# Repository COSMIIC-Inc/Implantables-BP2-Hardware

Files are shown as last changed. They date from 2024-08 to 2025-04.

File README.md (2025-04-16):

# Implantables-BP2-Hardware Read Me

## Contents
This repository is home to the 3D CAD and PCB design files of the BP2 - Biopotential Recording Module in the COSMIIC System.
Further documentation is available at **[docs.cosmiic.org/Implantables/BP2-Module](https://docs.cosmiic.org/Implantables/BP2-Module)**

## Licensing
Hardware-related files are licensed to open source users by COSMIIC under the CERN Open Hardware License - Permissive - v2 (CERN-OHL-P-2.0). Refer to the **[license text](https://ohwr.org/cern_ohl_p_v2.txt)** (also embedded in the repository as **LICENSE.txt**) and **[user guide](https://ohwr.org/project/cernohl/-/wikis/uploads/8a6b5d01f71c207c49493e4d114d61e6/cern_ohl_p_v2_howto.pdf)** to understand your permissions.

Hardware-related files includes, but is not limited to...

- Mechanical Design
    - 3D CAD Files (parts and assemblies, multiple file types)
    - Mechanical Drawings (parts and assemblies, mulitple file types)
- PCB Design
    - Fabrication (Gerber and Drill files)
    - Assembly (Pick and Place, BOM)
    - Archive (Schematics, multiple file types)

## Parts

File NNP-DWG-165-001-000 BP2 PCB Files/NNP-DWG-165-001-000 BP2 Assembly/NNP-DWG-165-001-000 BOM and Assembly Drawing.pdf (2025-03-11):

D | D

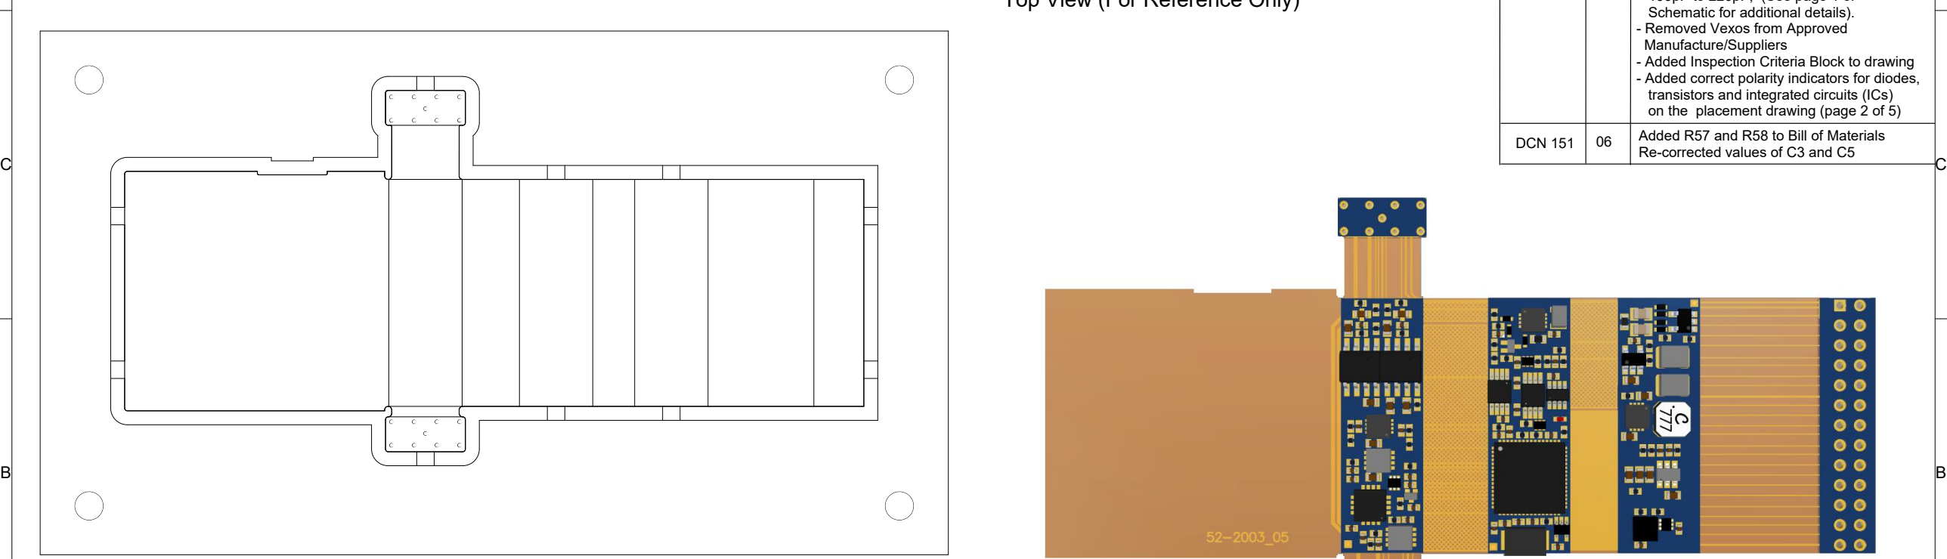
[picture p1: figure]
Schematic for additional details). - Removed Vexos from Approved Manufacture/Suppliers; transistors and integrated circuits (ICs) on the placement drawing (page 2 of 5); Re-corrected values of C3 and C5; DCN 151
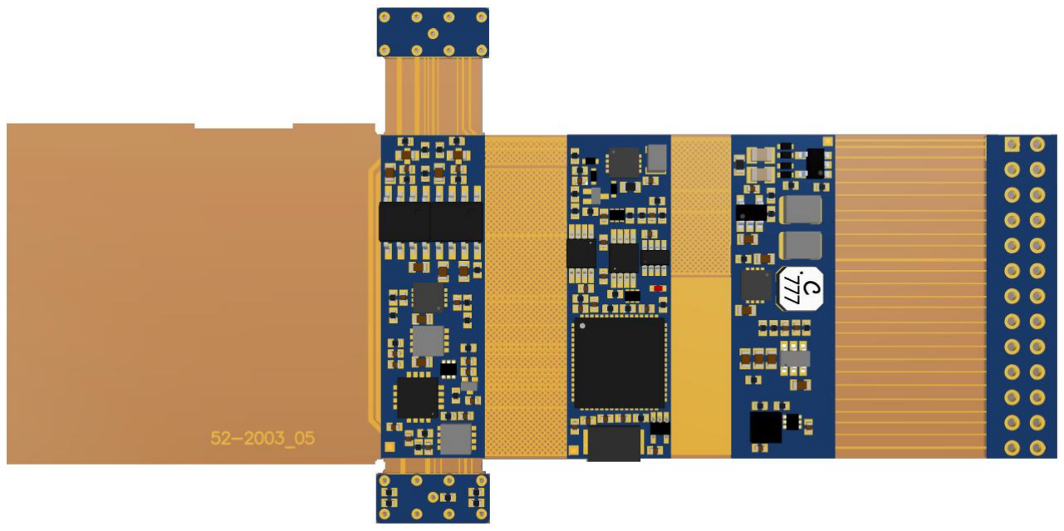
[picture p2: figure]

A | A
DRAWN K. Kowalski | 11-18-2022
CHECKED T. Crish | 11-18-2022
51-2003 | 06

Biopotential (BP2) PCB Assembly Drawing

DOCUMENT NAME

DOCUMENT NO. | REV

NEXT ASSY
SCALE:

B

SIZE
FINISH

MATERIAL

BY | DATE

SHEET 1 OF 5

ECN | REV | DESCRIPTION

N/A

1. Approved Manufacture/Suppliers.
Valtronic Technologies
2. Appropriate ESD precautions shall be used while building or handling this assembly.
3. PCB, Components and Solder must be RoHS 2 compliant.
4. Assembly shall be acceptable and rejectable per IPC-A-610, Class 3.
5. Components with pin 1 designator or polarization marking shall be placed as indicated on the assembly drawing.
6. Rework, repair or modifications must comply with IPC-7711 and IPC 7721.
7. Each PCB must be sequentially serialized and labeled as indicated on the purchase order.
8. Must supply testing certificate with every PCB assembly lot.
9. Supplier must notify and receive approval from Synapse Biomedical Inc before making any modifications to the design process or any changes to the materials used during the manufacturing of this assembly.
10. Do not populate C18, R26, and U10.
11. Do not populate R1-R10
12. Printed circuit boards (PCBs) shall be shipped in frames.
13. R57 is hand-soldered across pins 4 and 5 of U12.
14. R58 is hand-soldered across the gate and source of Q2.

Equivalent to CWRU VT901002

Build for BP2C Verification
- Removed Power-up reset circuit.
- Changed values of C1, C3, C5 and C6

DCN 101 03

- Updated BOM (refer to Page 1 of the Schematic for changes)
- Updated Manufacturing Notes
- Added PCB Frame and Outline Drawings
- Added instructions for serial number sticker.
- Added quantity to the BOM.
- Removed Software reference.
- Removed Inspection Criteria Block

DCN 107 04

N/A

DCN 121 05

- Add Pick and Place file to the BOM.
- Changed Capacitors C40 and C51 from 100pF to 220pF, (See page 1 of
- Added Inspection Criteria Block to drawing
- Added correct polarity indicators for diodes,

N/A

## Top View (For Reference Only)

E

INSPECTION REQUIRED | YES | NO
| X
CERTIFICATE REQUIRED | YES | NO
| X

Insp. Item
A | Inspect to current 51-2003-08 Inspection Procedure
| REF 51-2003-09 Inspect report
C | RoHS Certificate required

D

INSPECTION CRITERIA

06 Added R57 and R58 to Bill of Materials

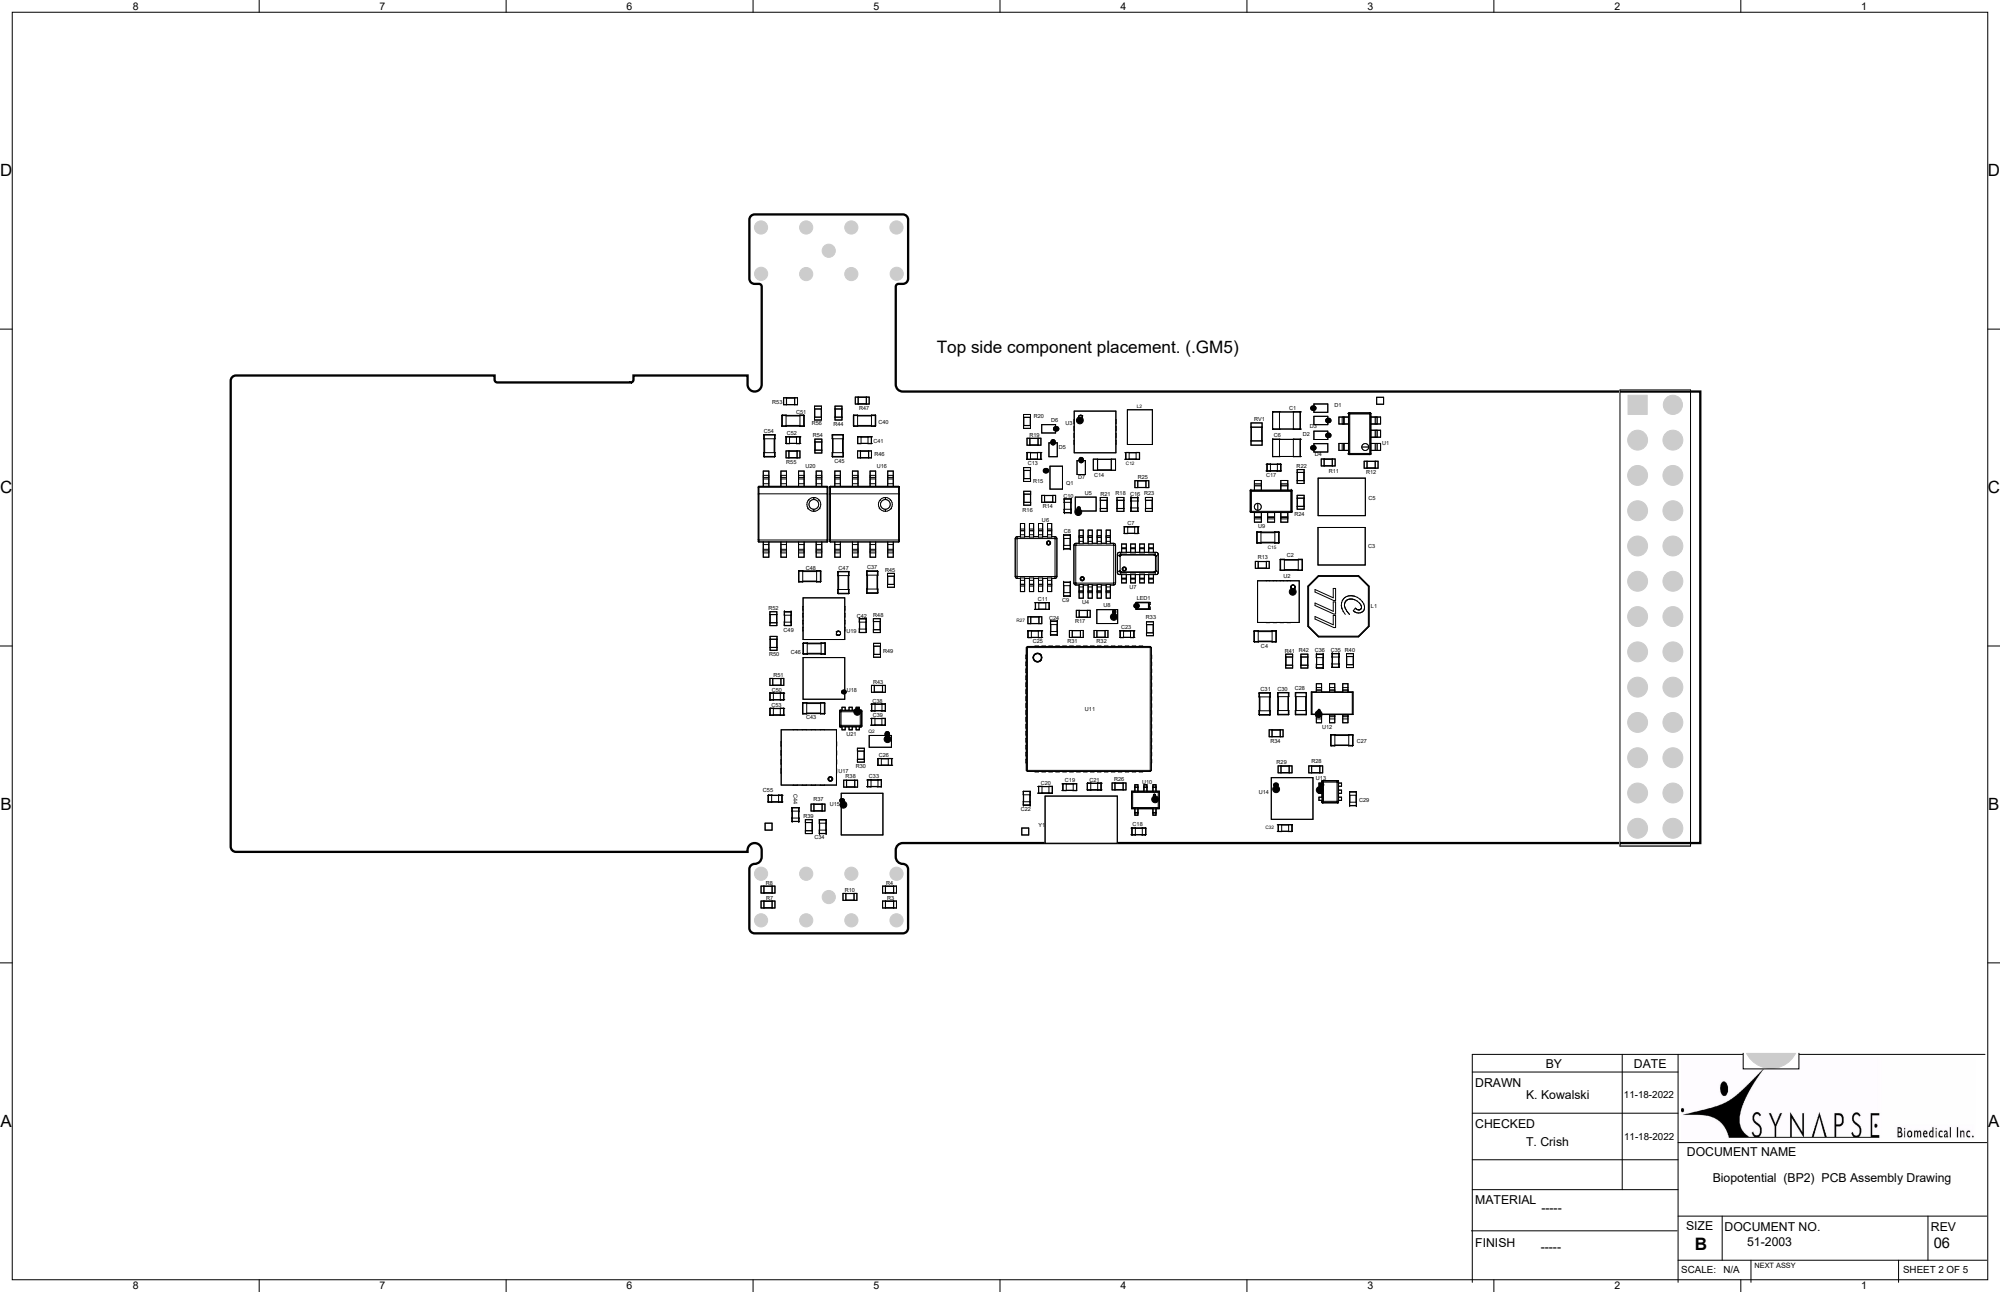
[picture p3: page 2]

Top side component placement. (.GM5)

DRAWN K. Kowalski | 11-18-2022

CHECKED T. Crish | 11-18-2022

DOCUMENT NAME
Biopotential (BP2) PCB Assembly Drawing

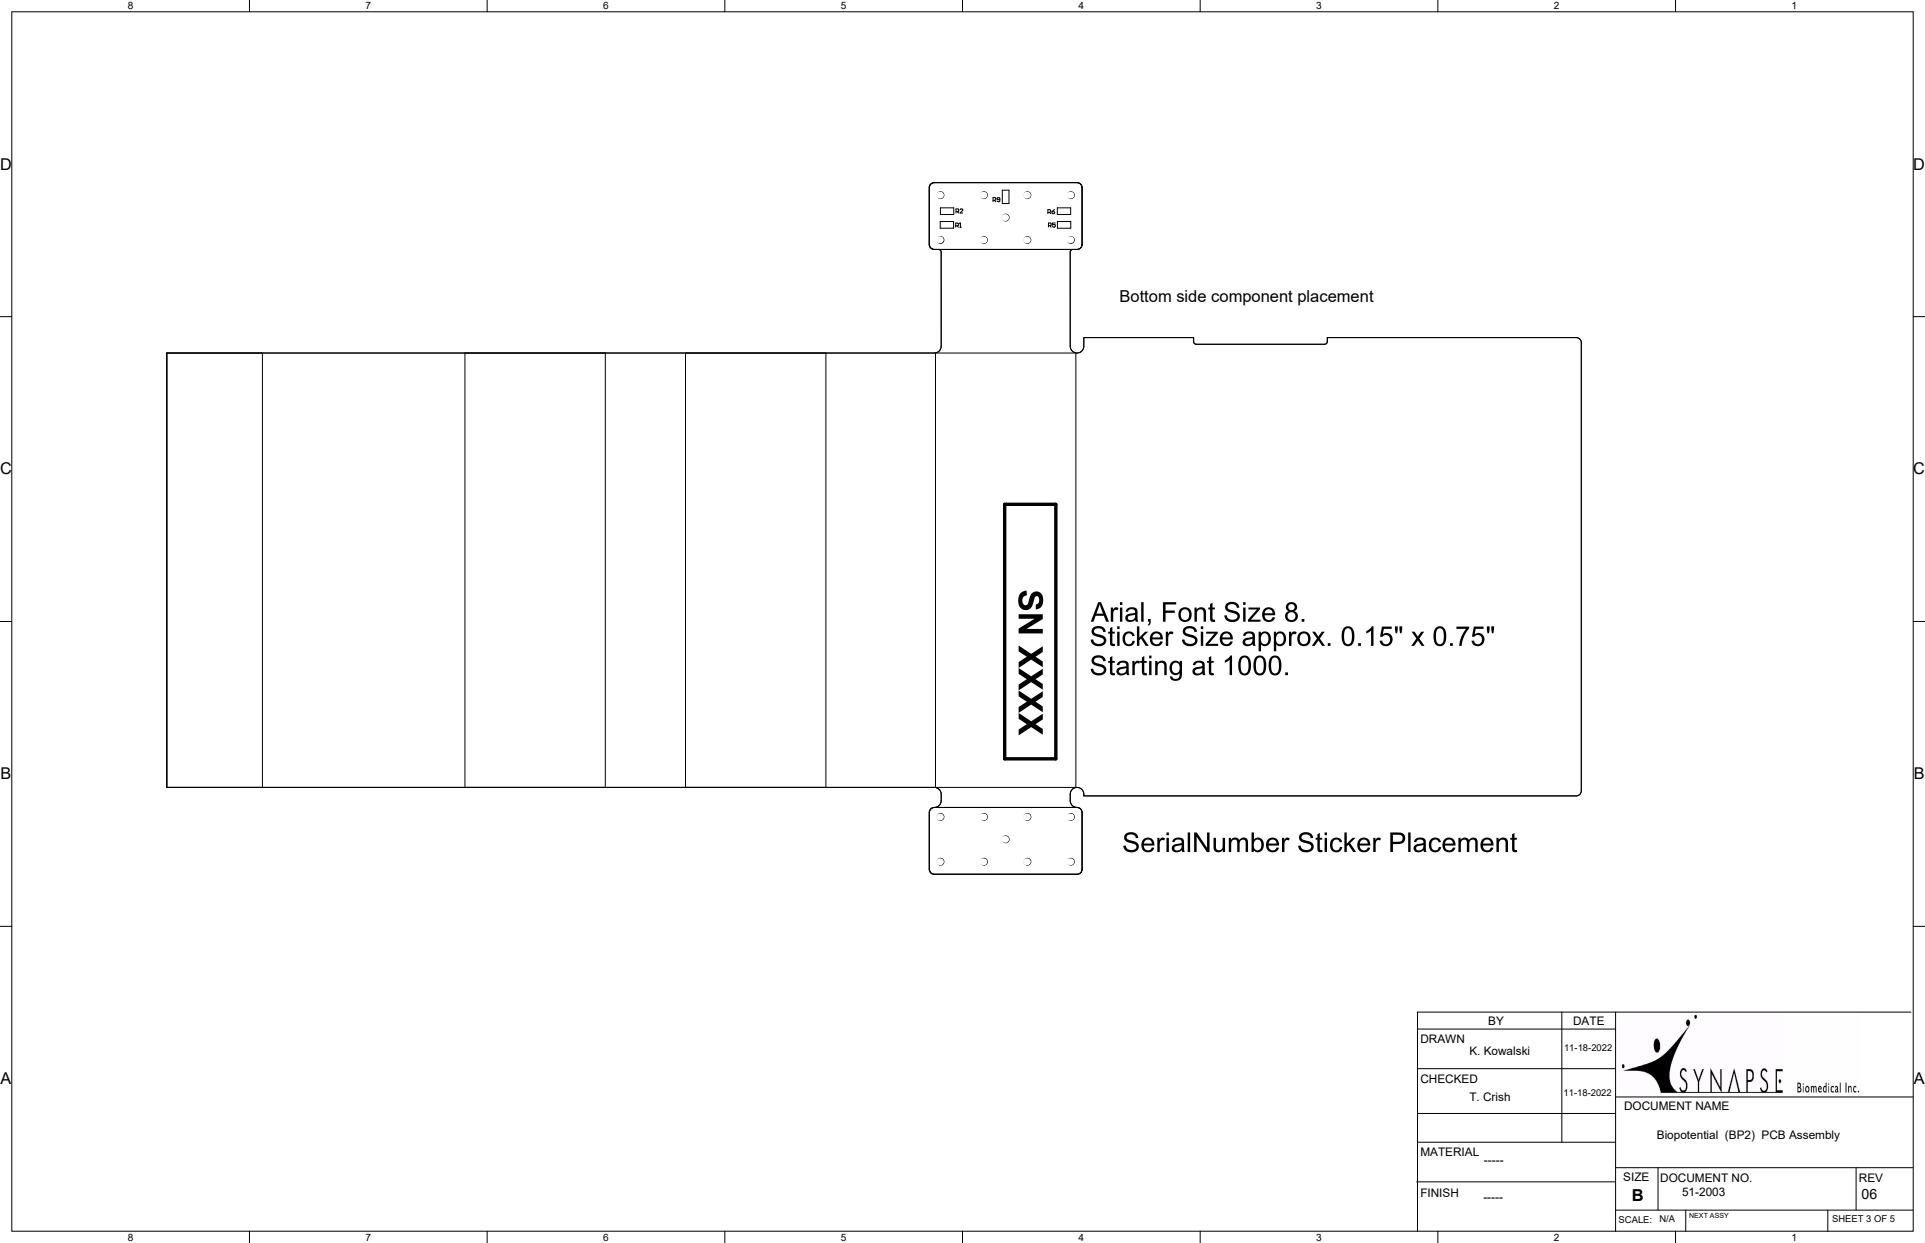
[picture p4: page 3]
DATE; DOCUMENT NAME

Bottom side component placement

DRAWN K. Kowalski | 11-18-2022

CHECKED T. Crish | 11-18-2022

Biopotential (BP2) PCB Assembly

D | D
C | C
B | B
A | A
BY | DATE
DRAWN K. Kowalski | 11-18-2022
CHECKED T. Crish | 11-18-2022

DOCUMENT NAME

Biopotential (BP2) PCB Assembly

Item

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
Designator

Ref.

Ref.

Ref.

C1, C6
C2, C14, C15, C28, C30, C31
C3, C5
C4, C27
C7, C8, C9, C10, C11, C20, C22, C23, C24, C29, C32, C34, C35, C38, C39, C42, C49, C50, C53
C12, C16
C13
C17
C19, C21
C25
C37, C43, C45, C46, C47, C48, C54 C36
C40, C51
C41, C52
C33, C44, C55
C26
D1, D2, D3, D4, D5, D6, D7 L1
L2
LED1
Q1

Q2

R1, R2, R3, R4, R5, R6, R7, R8, R9, R10 R11
R12, R17, R18, R19, R22, R25, R42 R13
R14, R20, R21, R23

SBI

51-2003-01_07

52-2003_05

51-2003-07_02

53-0097
53-0067
53-0068
53-0039
53-0040-1

53-0042
53-0041-1
53-0043
53-0044-1
53-0069
53-0070
53-0041-2
53-0071
53-0072
53-0040-2
53-0078
54-0075
53-0032
53-0033
53-0035
54-0050

54-0078

53-0048
53-0049-1
53-0049-2
53-0049-3
53-0049-4

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
Description

Biopotential (BP2) Schematic Drawing 51-2003-01_07
NNP Biopotential PCB, Unpopulated 52-2003_05
Biopotential (BP2) Pick and Place 51-2003-07_02 Biopotential (BP2) 0.1uF, 100V, X7R, 0805, 10%, RoHS 1.0uF, 50V, X7R, 0603, 20%, RoHs 22uF, 16V, X5R, 1210, 20%, RoHS 10uF, 6.3V, X5R, 0603_20%, RoHS 0.1uF, 16V, X7R,10%, 0402, RoHS

4.7uF, 6.3V, X5R, 20%, 0402, RoHS 68pF, 50V, C0G, 0402, 5%, RoHS 0.001uF, 50V, X7R, 20%, 0402, RoHS 8pF, 50V, C0G, 0402, 10%, RoHS 2.2uF, 6.3V, X5R, 0402, 20%, RoHS 0.15uF, 16V, X7R, 10%, 0603, RoHS 1000pF, 50V, C0G, 5%, 0402, RoHS X2Y, 220pF, 50V, X7R, 0603, 20%, RoHS 4700pF, 50V, C0G, 0402_10%, RoHS 0.15uF, 16V, X7R, 10%, 0402, RoHS 1.0uF, 6.3V, X5R, 0402, 20%, RoHS Schotty Diode, 30V, 100mA, RoHS 100uH, 270mA, 20%, RoHS
470uH, 35mA, 10%, RoHS
LED, Red, 0402, 20mA ,2V, 140mcd, RoHS PNP, -50V, -100mA, SOT523, 150MHz, RoHS
Small Signal MOSFET, -20 V, -760 mA, P-Channel, Gate Zener
0.0 ohm, 1/16W, 0402, RoHS
0.1 ohm, 1%, 1/16W, 0402, RoHS
49.9k ohm, 1%, 1/16W, 0402, RoHS 470k ohm, 1% , 1/16W, smd, 0402, RoHS 1.0k ohm, 1%, 1/16W, smd, 0402, RoHS

Manufacture

N/A

See Note 1

N/A

Murata Electronics North America Taioyo Yuden
Taioyo Yuden
Murata Electronics North America Murata Electronics North America

Murata Electronics North America Murata Electronics North America Murata Electronics North America Murata Electronics North America Murata Electronics North America Samsung-Electro-Mechanics
Murata Electronics North America Johanson Dielectrics Inc.
Murata Electronics North America Samsung-Electro-Mechanics
Murata Electronics North America Panasonic Electronic Components TDK Corporation
Taiyo Yuden
Lumex Opto/Components Inc. Panasonic Electronic Components

ON Semiconductor

Vishay Dale
Vishay Dale
Vishay Dale
Vishay Dale
Vishay Dale

Manufacturer Part Number

N/A

N/A

N/A

GCM21BR72A104KA37K
UMK107AB7105KA-T
EMK325BJ226MD-T
GRM188R60J106ME47J
GRM155R71C104KA88D

GRM155R60J475ME47D
GRM1555C1H680JA01D
GJM1555C1H1R0BB01D
GRM1555C1H8R0DA01D
GRM155R60J225ME15D
CL05B154KO5NNNC
GRM1555C1H102JA01D
500X14W221MV4T
GRM155R71H472KA01D
CL05B154KO5NNNC
GRM155R60J105ME19D
DB2731600L
VLCF5020T-101MR27
CB2518T471K
SML-LX0402SIC-TR
DSA9001S0L

NTE4151PT1G

CRCW04020000Z0ED
RCWE0402R100FNEA
CRCW040249K9FKED
CRCW0402470KFKED
CRCW04021K00FKED

Suggested
Supplier
N/A

See Note 1

N/A

Digi-Key
Digi-Key
Digi-Key
Digi-Key
Digi-Key

Digi-Key
Digi-Key
Digi-Key
Digi-Key
Digi-Key
Digi-Key
Digi-Key
Digi-Key
Digi-Key
Digi-Key
Digi-Key
Digi-Key
Digi-Key
Digi-Key
Digi-Key
Digi-Key

Digi-Key

Digi-Key
Digi-Key
Digi-Key
Digi-Key
Digi-Key

Supplier Part Number

N/A

N/A

N/A

490-8051-2-ND
587-5956-6-ND
587-2412-1-ND
490-6405-6-ND
490-3261-6-ND

490-5915-6-ND
490-5876-6-ND
490-6073-6-ND
490-5867-6-ND
490-4519-6-ND
1276-6651
490-3244-6-ND
500X14W221MV4T-ND
490-1308-6-ND
1276-6651-6-ND
490-5955-6-ND
DB2731600LDKR-ND
445-3203-6-ND
587-2194-6-ND
67-1878-6-ND
DSA9001S0LDKR-ND

NTE4151PT1GOSDKR-ND

541-0.0JDKR-ND
541-2711-6-ND
541-49.9KLDKR-ND
541-470KLDKR-ND
541-1.00KLDKR-ND

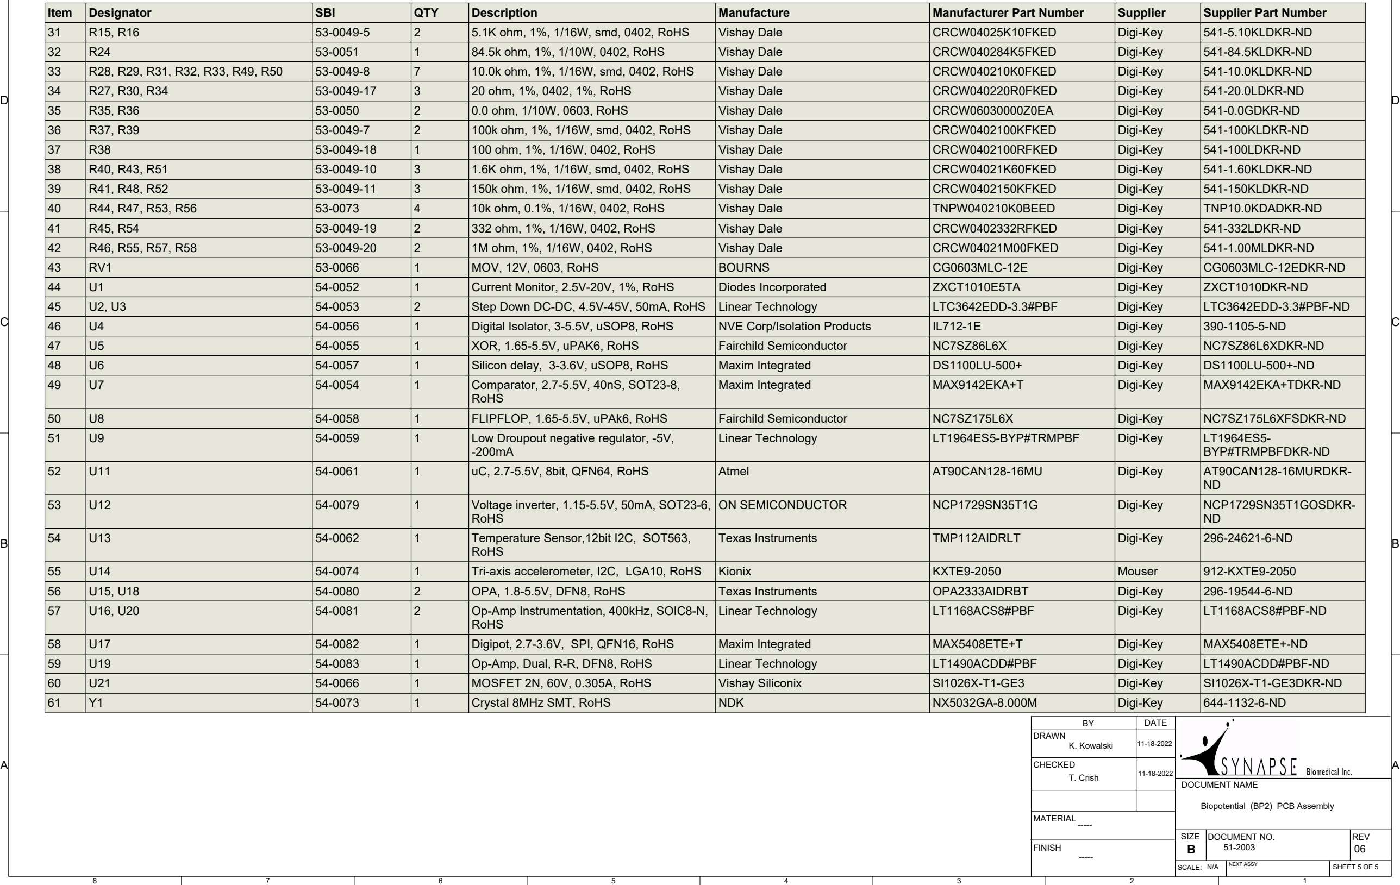
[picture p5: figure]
DATE; CHECKED T. Crish; DRAWN K. Kowalski; DOCUMENT NAME; Biopotential (BP2) PCB Assembly; Item; Designator R15, R16 R24 R28, R29, R31, R32, R33, R49, R50 R27, R30, R34 R35, R36 R37, R39 R38 R40, R43, R51 R41, R48, R52 R44, R47, R53, R56 R45, R54 R46, R55, R57, R58 RV1 U1 U2, U3 U4 U5 U6 U7; SBI 53-0049-5 53-0051 53-0049-8 53-0049-17 53-0050 53-0049-7 53-0049-18 53-0049-10 53-0049-11 53-0073 53-0049-19 53-0049-20 53-0066 54-0052 54-0053 54-0056 54-0055 54-0057 54-0054; QTY; Description 5.1K ohm, 1%, 1/16W, smd, 0402, RoHS 84.5k ohm, 1%, 1/10W, 0402, RoHS 10.0k ohm, 1%, 1/16W, smd, 0402, RoHS 20 ohm, 1%, 0402, 1%, RoHS 0.0 ohm, 1/10W, 0603, RoHS 100k ohm, 1%, 1/16W, smd, 0402, RoHS 100 ohm, 1%, 1/16W, 0402, RoHS 1.6K ohm, 1%, 1/16W, smd, 0402, RoHS 150k ohm, 1%, 1/16W, smd, 0402, RoHS 10k ohm, 0.1%, 1/16W, 0402, RoHS 332 ohm, 1%, 1/16W, 0402, RoHS 1M ohm, 1%, 1/16W, 0402, RoHS MOV, 12V, 0603, RoHS Current Monitor, 2.5V-20V, 1%, RoHS Step Down DC-DC, 4.5V-45V, 50mA, RoHS Digital Isolator, 3-5.5V, uSOP8, RoHS XOR, 1.65-5.5V, uPAK6, RoHS Silicon delay, 3-3.6V, uSOP8, RoHS Comparator, 2.7-5.5V, 40nS, SOT23-8, RoHS FLIPFLOP, 1.65-5.5V, uPAk6, RoHS Low Droupout negative regulator, -5V, -200mA uC, 2.7-5.5V, 8bit, QFN64, RoHS; Voltage inverter, 1.15-5.5V, 50mA, SOT23-6, RoHS Temperature Sensor,12bit I2C, SOT563, RoHS Tri-axis accelerometer, I2C, LGA10, RoHS OPA, 1.8-5.5V, DFN8, RoHS Op-Amp Instrumentation, 400kHz, SOIC8-N, RoHS Digipot, 2.7-3.6V, SPI, QFN16, RoHS Op-Amp, Dual, R-R, DFN8, RoHS MOSFET 2N, 60V, 0.305A, RoHS Crystal 8MHz SMT, RoHS; Manufacture Vishay Dale Vishay Dale Vishay Dale Vishay Dale Vishay Dale Vishay Dale Vishay Dale Vishay Dale Vishay Dale Vishay Dale Vishay Dale Vishay Dale BOURNS Diodes Incorporated Linear Technology NVE Corp/Isolation Products Fairchild Semiconductor Maxim Integrated Maxim Integrated; Fairchild Semiconductor Linear Technology; Atmel; ON SEMICONDUCTOR; Texas Instruments; Kionix Texas Instruments Linear Technology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

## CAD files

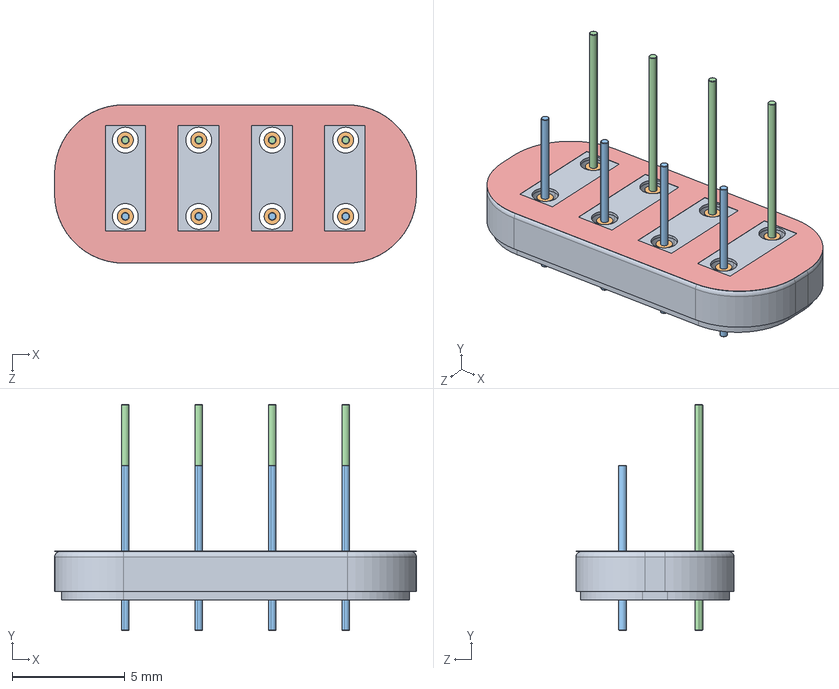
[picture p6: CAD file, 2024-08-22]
Mechanical Design CAD Files/STEP Files/NNP-DWG-135-001-001 SA, Remote Module, Capthrough Sandblasted.STEP
16.0 x 10.0 x 7.01 mm
NNP-DWG-130-010-000 Remote Module, Capthrough, Lid
NNP-DWG-130-008-000 Capthrough, Ceramic x 8
NNP-DWG-130-009-001 Capthrough, Pin, Ring x 4
NNP-DWG-130-009-002 Capthrough, Pin, Jogged_PRE-BENT x 4
NNP-MAT-150-017-000 150 Micron Aluminum Oxide

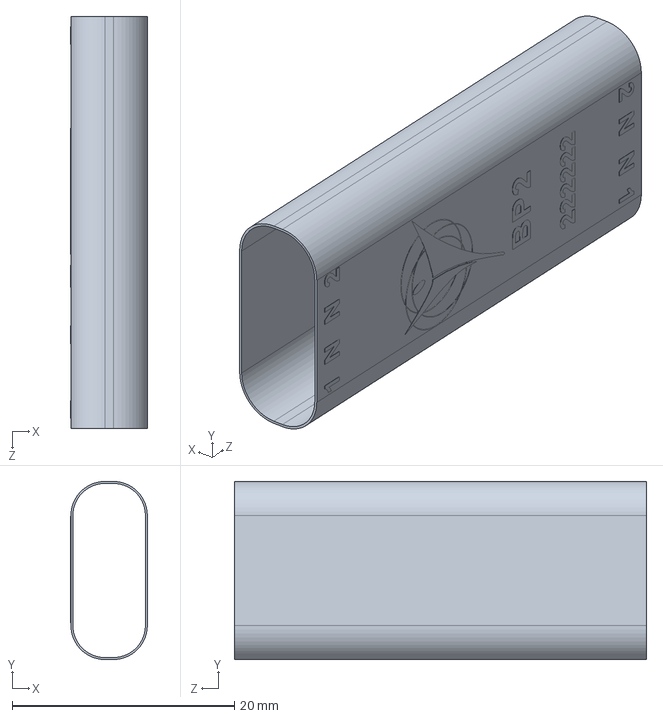
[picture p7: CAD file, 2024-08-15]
Mechanical Design CAD Files/STEP Files/NNP-DWG-160-001-000 Remote Module, Case, BP2 Marking.STEP
6.91 x 16.0 x 37.1 mm

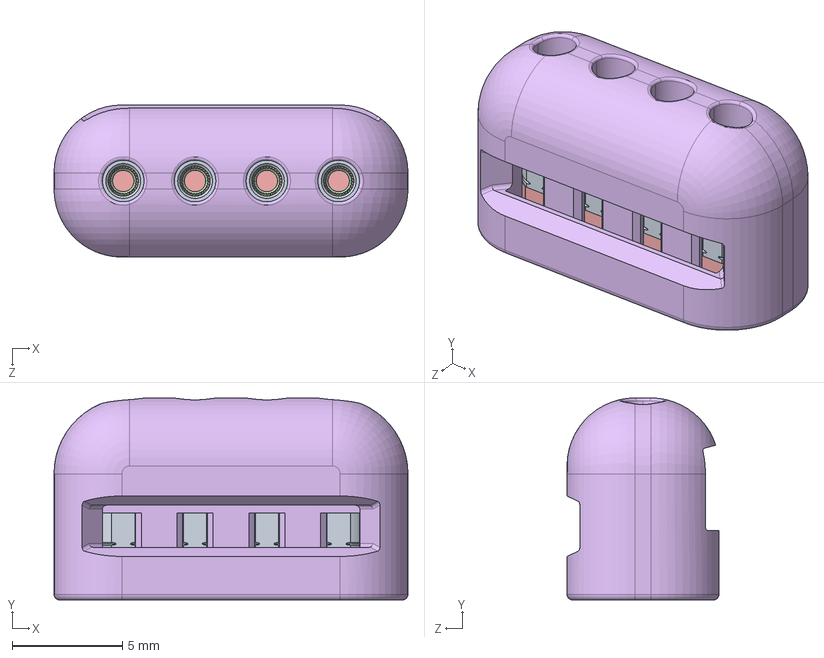
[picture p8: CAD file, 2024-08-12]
Mechanical Design CAD Files/STEP Files/NNP-DWG-135-005-000 SA, Remote Module, Header.STEP
16.0 x 9.14 x 6.88 mm
NNP-DWG-130-011-000 Balseal, Conductor x 8
NNP-DWG-130-012-001 Balseal, Spring, CW x 4
NNP-DWG-130-013-001 Balseal, Washer, CW x 4
NNP-DWG-130-013-002 Balseal, Washer, CCW x 4
NNP-DWG-130-012-002 Balseal, Spring, CCW x 4
NNP-DWG-130-005-000 BalSeal Assembly, Internal Cavity Single Seal_COMPRESSED x 4
NNP-DWG-130-004-000 Remote Module, Pre-Molded Header Cap
NNP-DWG-130-003-000 Remote Module, Pre-Molded Header Body
NNP-DWG-130-006-000 Remote Module, Header, Gasket_GASKET x 8

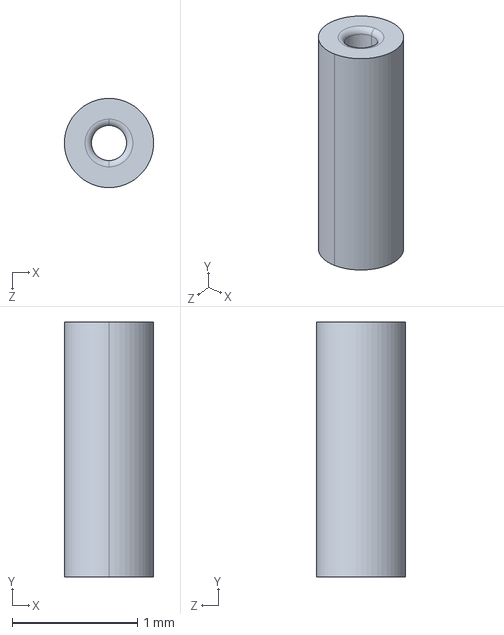
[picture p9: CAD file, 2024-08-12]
Mechanical Design CAD Files/STEP Files/NNP-DWG-130-008-000 Capthrough, Ceramic.STEP
0.711 x 2.03 x 0.711 mm

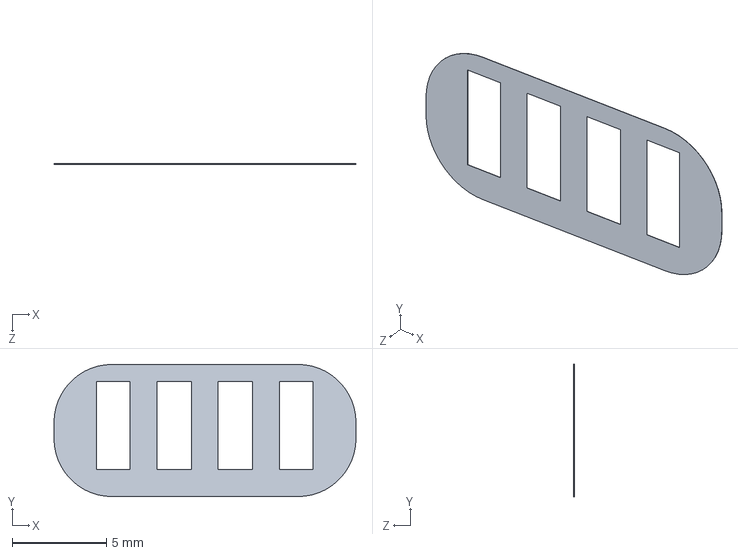
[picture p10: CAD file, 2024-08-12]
Mechanical Design CAD Files/STEP Files/NNP-MAT-150-017-000 150 Micron Aluminum Oxide.STEP
16.0 x 7.01 x 0.0127 mm

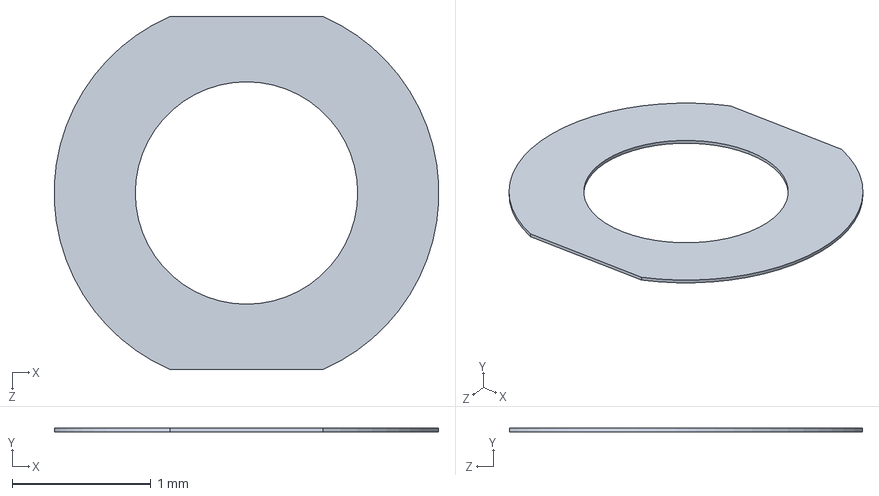
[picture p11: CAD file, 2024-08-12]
Mechanical Design CAD Files/STEP Files/NNP-DWG-130-006-000 Remote Module, Header, Gasket.STEP
2.77 x 0.0254 x 2.54 mm

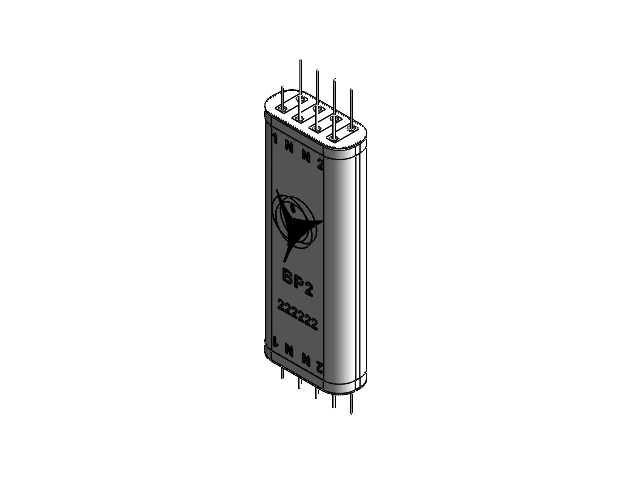
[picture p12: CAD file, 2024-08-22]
Mechanical Design CAD Files/SolidWorks Native Files/NNP-DWG-165-002-001 SA, BP2 Module, Tack Weld Assembly.SLDASM
NNP-DWG-130-001-000 Remote Module, Case
NNP-DWG-130-010-000 Remote Module, Capthrough, Lid x 2
NNP-DWG-130-008-000 Capthrough, Ceramic x 16
NNP-DWG-130-009-001 Capthrough, Pin, Ring x 8
NNP-DWG-130-009-002 Capthrough, Pin, Jogged x 8
NNP-MAT-150-017-000 150 Micron Aluminum Oxide x 2
NNP-MAT-150-008-000 EPO-TEK 301 x 2
NNP-DWG-165-001-000 Remote Module, BP2, Flexible Circuit Assembly
NNP-DWG-130-002-000 Remote Module, Insulator Flex x 2
NNP-MAT-150-006-000 70% Isopropyl Alochol x 2
NNP-MAT-150-005-000 Distilled Water

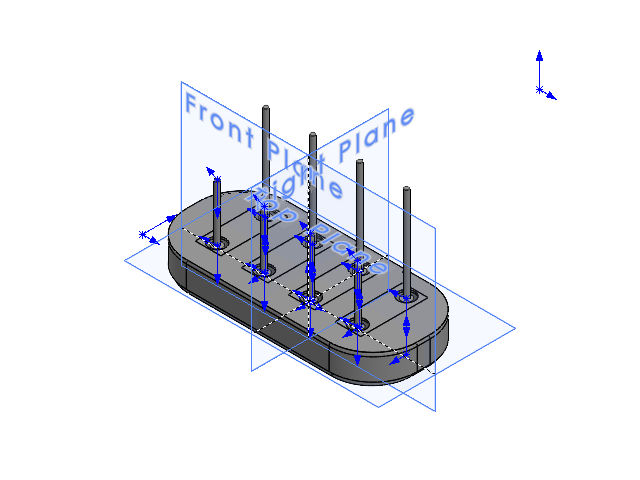
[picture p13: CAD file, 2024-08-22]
Mechanical Design CAD Files/SolidWorks Native Files/NNP-DWG-135-001-001 SA, Remote Module, Capthrough Sandblasted.SLDASM
NNP-DWG-130-010-000 Remote Module, Capthrough, Lid
NNP-DWG-130-008-000 Capthrough, Ceramic x 8
NNP-DWG-130-009-001 Capthrough, Pin, Ring x 4
NNP-DWG-130-009-002 Capthrough, Pin, Jogged x 4
NNP-MAT-150-017-000 150 Micron Aluminum Oxide
NNP-MAT-150-008-000 EPO-TEK 301

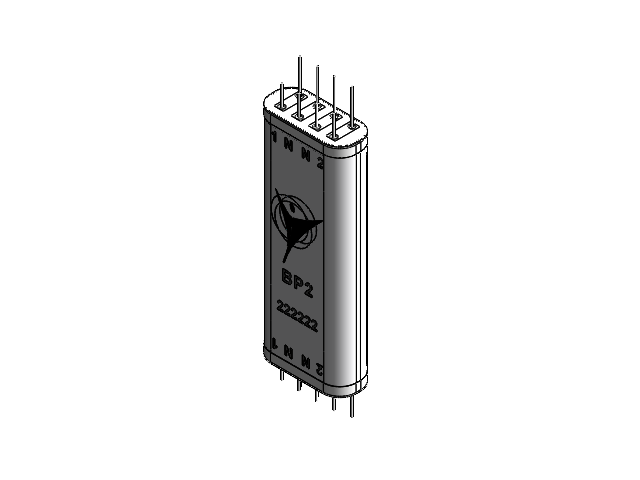
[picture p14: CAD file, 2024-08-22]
Mechanical Design CAD Files/SolidWorks Native Files/NNP-DWG-165-002-000 SA, BP2 Module, Weld Assembly.SLDASM
NNP-DWG-130-001-000 Remote Module, Case
NNP-DWG-130-010-000 Remote Module, Capthrough, Lid x 2
NNP-DWG-130-008-000 Capthrough, Ceramic x 16
NNP-DWG-130-009-001 Capthrough, Pin, Ring x 8
NNP-DWG-130-009-002 Capthrough, Pin, Jogged x 8
NNP-MAT-150-017-000 150 Micron Aluminum Oxide x 2
NNP-MAT-150-008-000 EPO-TEK 301 x 2
NNP-DWG-165-001-000 Remote Module, BP2, Flexible Circuit Assembly
NNP-DWG-130-002-000 Remote Module, Insulator Flex x 2
NNP-MAT-150-006-000 70% Isopropyl Alochol x 2
NNP-MAT-150-005-000 Distilled Water

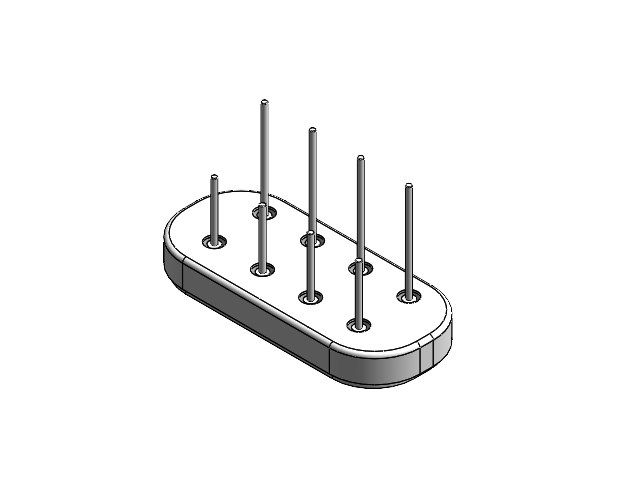
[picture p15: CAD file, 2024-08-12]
Mechanical Design CAD Files/SolidWorks Native Files/NNP-DWG-135-001-000 SA, Remote Module, Capthrough.SLDASM
NNP-DWG-130-010-000 Remote Module, Capthrough, Lid
NNP-DWG-130-008-000 Capthrough, Ceramic x 8
NNP-DWG-130-009-001 Capthrough, Pin, Ring x 4
NNP-DWG-130-009-002 Capthrough, Pin, Jogged x 4

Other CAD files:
Mechanical Design CAD Files/SolidWorks Native Files/NNP-DWG-160-001-000 Remote Module, Case, BP2 Marking.SLDASM
Mechanical Design CAD Files/SolidWorks Native Files/NNP-DWG-130-008-000 Capthrough, Ceramic.SLDPRT
Mechanical Design CAD Files/STEP Files/NNP-DWG-130-001-000 Remote Module, Case, No Marking.STEP
Mechanical Design CAD Files/STEP Files/NNP-DWG-130-001-000 Remote Module, Case.STEP
Mechanical Design CAD Files/STEP Files/NNP-DWG-130-002-000 Remote Module, Insulator Flex.STEP
Mechanical Design CAD Files/STEP Files/NNP-DWG-130-003-000 Remote Module, Pre-Molded Header Body.STEP
Mechanical Design CAD Files/STEP Files/NNP-DWG-130-004-000 Remote Module, Pre-Molded Header Cap.STEP
Mechanical Design CAD Files/STEP Files/NNP-DWG-130-007-000 Remote Module, Suture Skirt.STEP
Mechanical Design CAD Files/STEP Files/NNP-DWG-130-009-001 Capthrough, Pin, Ring.STEP
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

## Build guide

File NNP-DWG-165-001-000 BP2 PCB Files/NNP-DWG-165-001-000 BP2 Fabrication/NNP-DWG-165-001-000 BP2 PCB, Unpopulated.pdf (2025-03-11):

88

77

66

D

C

B

A

1. Approved Manufacture/Supplier
Innovative Circuits Inc
2. Board Technology
A. Fabricate Rigid-Flex PCB in accordance with IPC-6013 and
IPC 2223, Type 4, Class 3
B. Maximum overall rigid thickness shall not exceed 18 mil. This is measured over finished plated surfaces. The maximum overall flexible thickness shall not exceed 5.0 mil
C. Finished hole size unless noted should be +/- 3 mil (0.076mm)
D. All materials must be compliant with the European Union RoHS 2 directive, 2011/65/EU
E. Finish shall be ENIG
1. Electroless nickel thickness inaccordance with IPC-4552
2 Immersion Gold thickness in accordance with IPC-4552
F. Soldermask shall be Blue on both sides in accordance with IPC-SM-840 Class H.
G. Silkscreen:
Primary Side (Top) - No silkscreen
Secondary Side (Bottom) - Manufacture ID and date code
H. Print Manufacture ID and Date Code on Bottom Layer, see page 4 of 8 for location.
I. Supplier must notify and receive approval from Synapse Biomedical Inc. before making any modifications to the design process or any changes to the materials used during
the manufacturing of this assembly.
3. Certificate of Conformity:
A. Complete description of the item with revision
B. Number of lot and Date Code
C. Delivered quantity
D. RoHS compliance
E. Remark/Exception as concession note
F. Name of the responsible with signature and date
4. Inspection Report:
A. Type of used base material and metallizations processes
1. Brand, reference and lot number of used base material
2. Used metallization and processes (chemical/galvanic) on Cu, Ni and Au
B. Visual checks and results:
1. Aspect (contamination, color, asperities, residues, mark, scraping, repair, etc.)
2. Open, short-circuit, etching non-conformities
3. Metallization adherence in accordance with IPC-TM-650 -- Method 2.4.1
4. Solder mask adherence in accordance with IPC-TM-650 -- Method 2.4.28.1
C. Dimensional checks and results:
1. Length and width of Strip
2. Length, width and total thickness of circuit
3. Diameter of index holes.
4. The thickness of nickel and gold metallizations shall be measured in accordance with IPC-4552 and a report of the measurements shall be provided.
D. Electrical Test:
1. Continuity and shorts 100% tested.
5. Micro section report:
A. Configuration of stack-up with measurements of different thicknesses
B. Thickness of Copper metallization.
6. Solderability test report:
A. Result of the solderability test according to ANSI/J-STD-003 -- Category 2 Test A -Hand Dipped

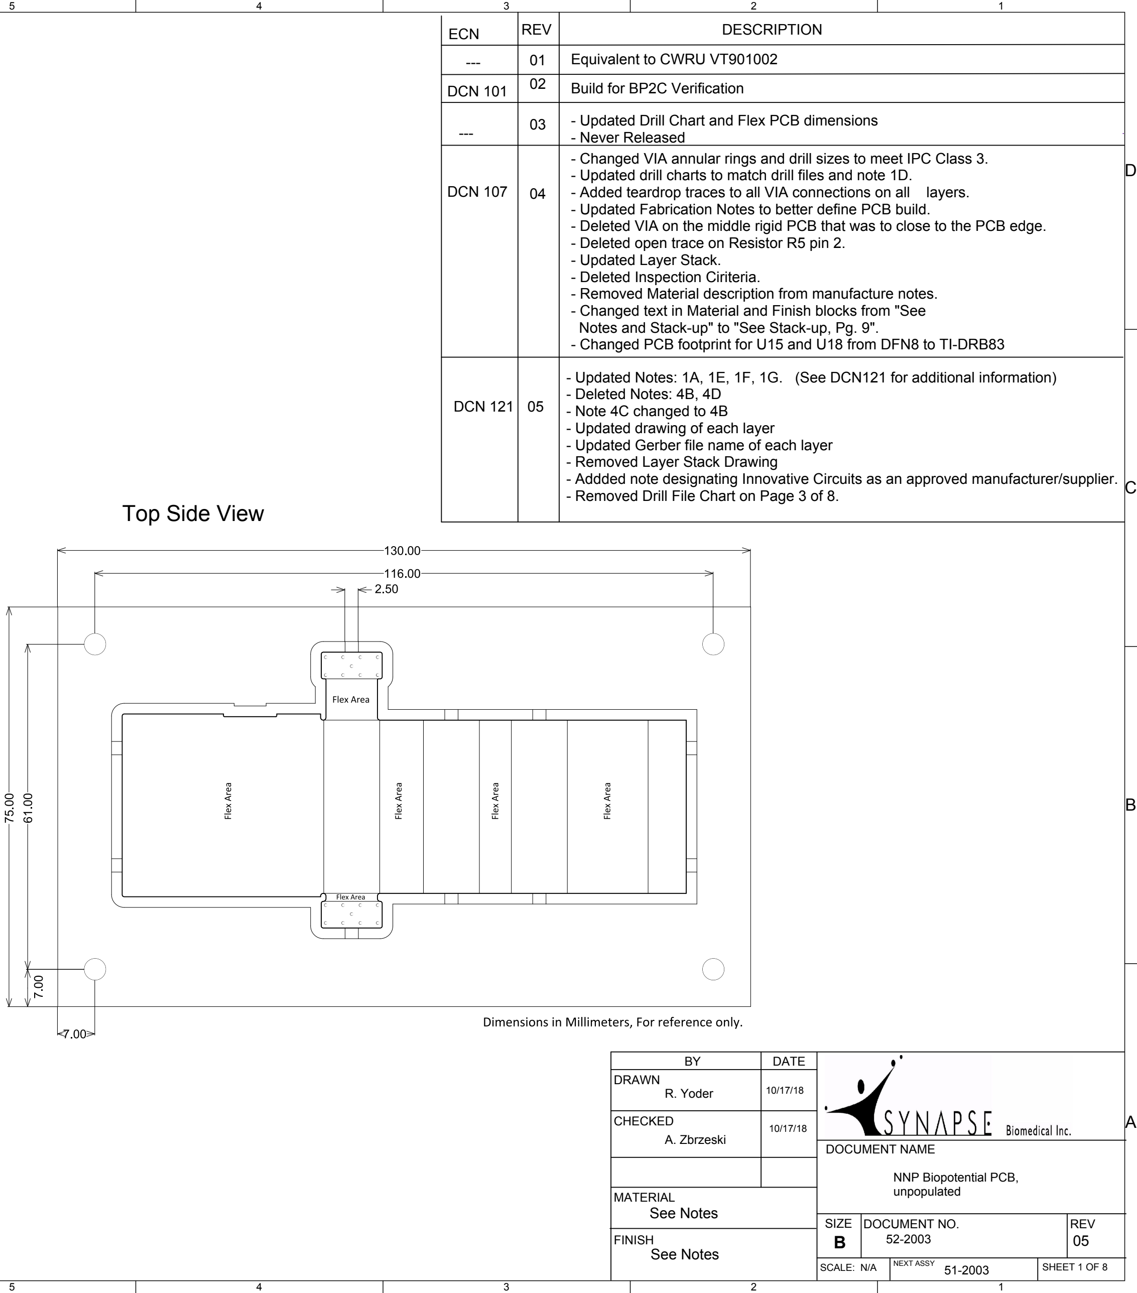
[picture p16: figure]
DRAWN R. Yoder; NNP Biopotential PCB, unpopulated; DOCUMENT NAME; DOCUMENT NO.; REV; NEXT ASSY; SCALE: B; SIZE; DATE; SHEET 1 OF 8; ECN; DESCRIPTION; DCN 101; Equivalent to CWRU VT901002; Build for BP2C Verification; - Never Released; - Updated Layer Stack. - Deleted Inspection Ciriteria.; DCN 107; See Notes; CHECKED A. Zbrzeski; MATERIAL; FINISH; Top Side View; DCN 121; - Deleted Notes: 4B, 4D - Note 4C changed to 4B - Updated drawing of each layer; - Removed Layer Stack Drawing

03 - Updated Drill Chart and Flex PCB dimensions

- Changed VIA annular rings and drill sizes to meet IPC Class 3.
- Updated drill charts to match drill files and note 1D.
- Added teardrop traces to all VIA connections on all layers.
- Updated Fabrication Notes to better define PCB build.
- Deleted VIA on the middle rigid PCB that was to close to the PCB edge.
- Deleted open trace on Resistor R5 pin 2.
- Removed Material description from manufacture notes.
- Changed text in Material and Finish blocks from "See
| Notes and Stack-up" to "See Stack-up, Pg. 9".
- Changed PCB footprint for U15 and U18 from DFN8 to TI-DRB83
- Updated Notes: 1A, 1E, 1F, 1G. (See DCN121 for additional information)
- Updated Gerber file name of each layer
- Addded note designating Innovative Circuits as an approved manufacturer/supplier.
- Removed Drill File Chart on Page 3 of 8.

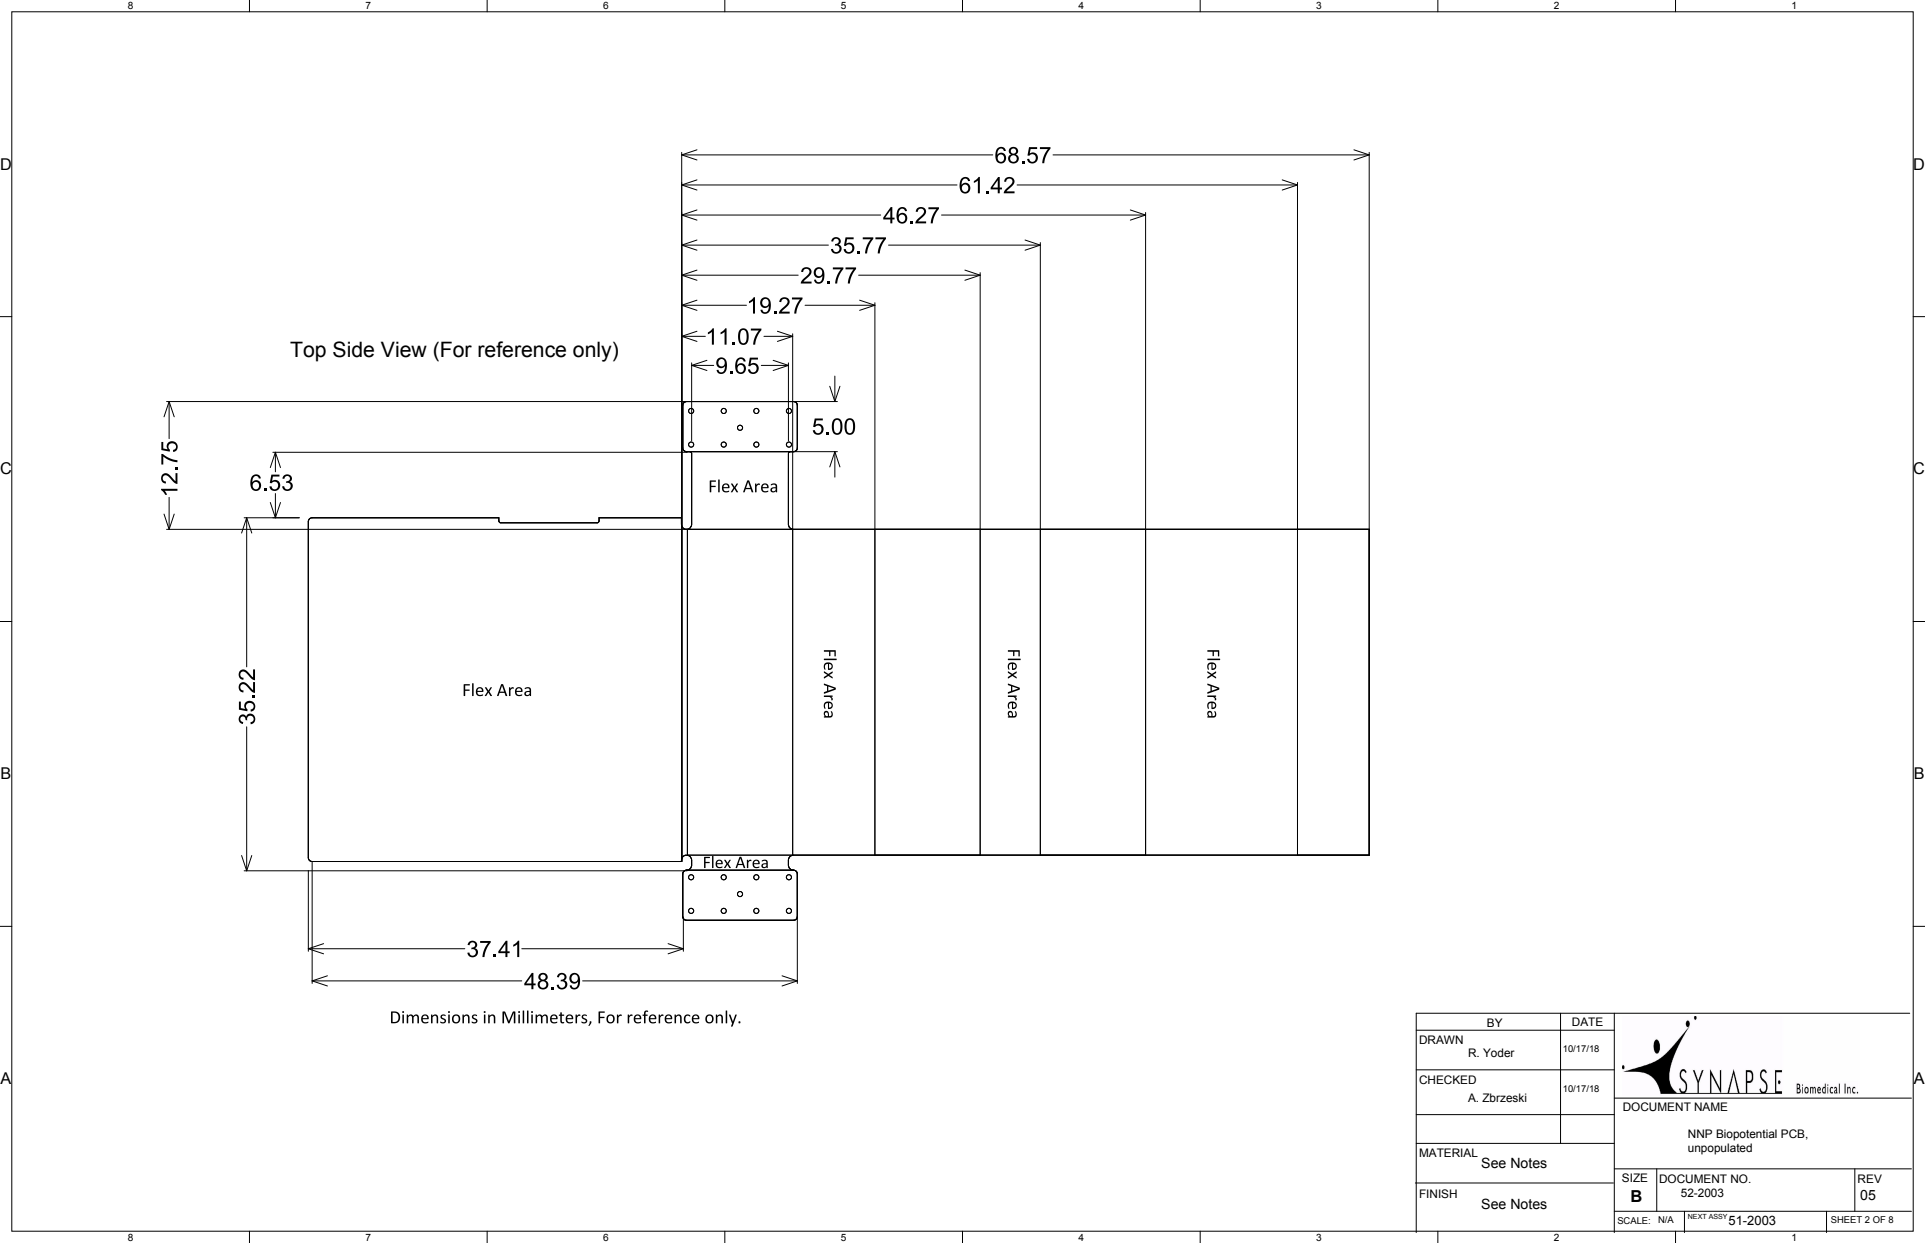
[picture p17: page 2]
SHEET 2 OF 8; DATE; SCALE:; DOCUMENT NAME

Top Side View (For reference only)

DRAWN R. Yoder | 10/17/18

CHECKED A. Zbrzeski | 10/17/18

NNP Biopotential PCB,

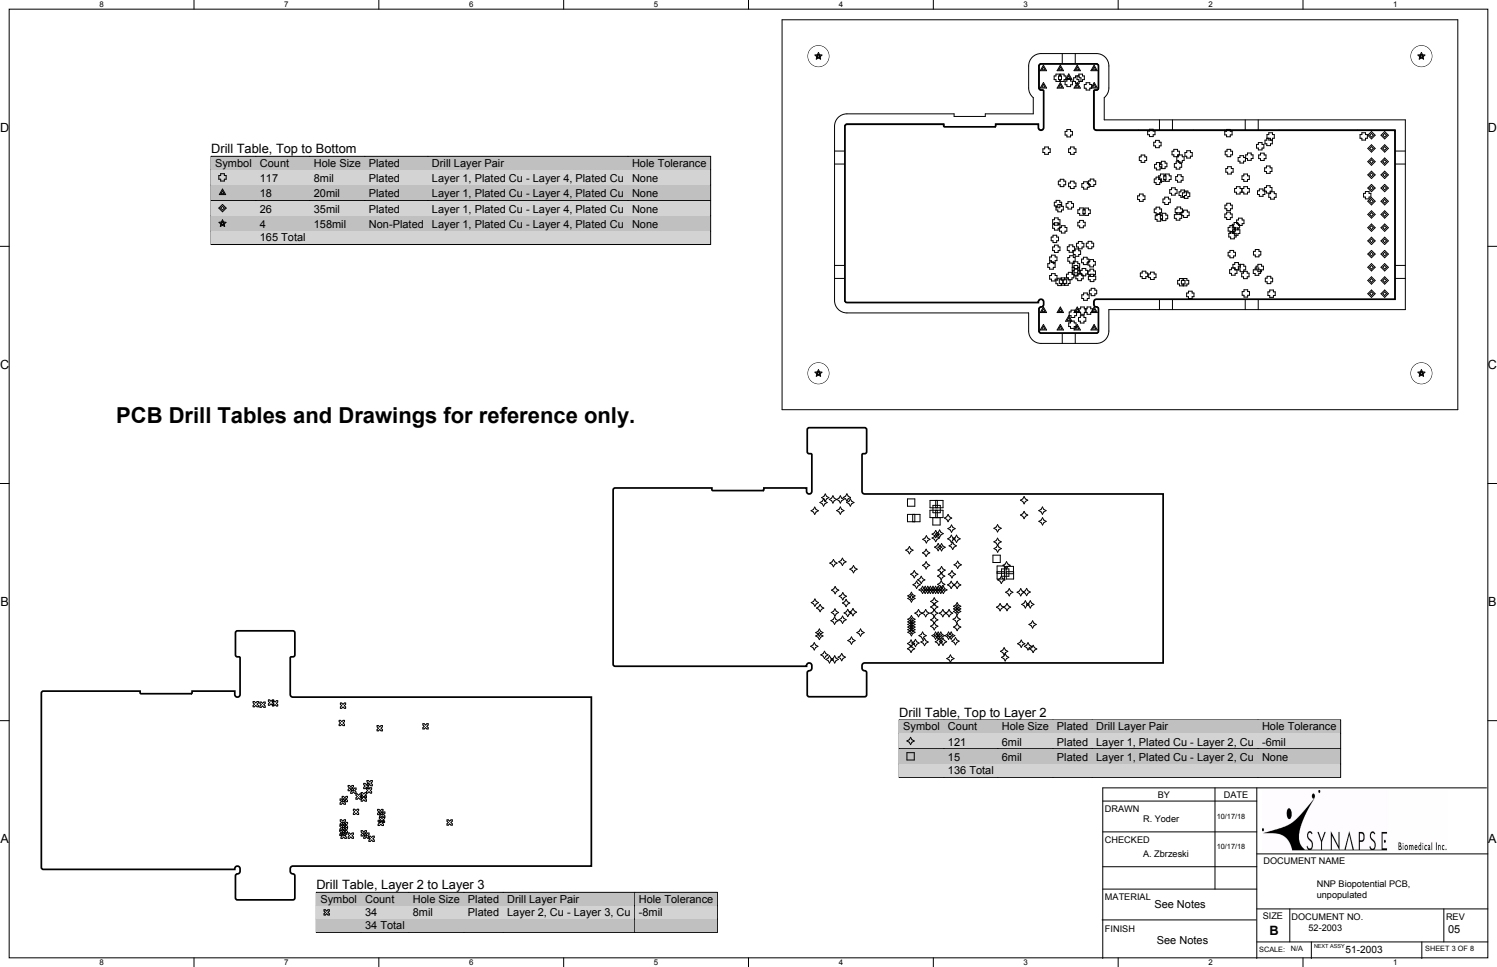
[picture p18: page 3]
DATE; DOCUMENT NAME

Drill Table, Top to Bottom

Symbol | Count | Hole Size | Plated | Drill Layer Pair | Hole Tolerance

117 | 8mil | Plated | Layer 1, Plated Cu - Layer 4, Plated Cu | None
18 | 20mil | Plated | Layer 1, Plated Cu - Layer 4, Plated Cu | None
26 | 35mil | Plated | Layer 1, Plated Cu - Layer 4, Plated Cu | None
4 | 158mil | Non-Plated | Layer 1, Plated Cu - Layer 4, Plated Cu | None
165 Total

PCB Drill Tables and Drawings for reference only.

Drill Table, Top to Layer 2

121 | 6mil | Plated | Layer 1, Plated Cu - Layer 2, Cu | -6mil
15 | 6mil | Plated | Layer 1, Plated Cu - Layer 2, Cu | None
136 Total

DRAWN R. Yoder | 10/17/18

CHECKED A. Zbrzeski | 10/17/18

Drill Table, Layer 2 to Layer 3

NNP Biopotential PCB,

8mil | Plated | Layer 2, Cu - Layer 3, Cu | -8mil

34 Total

## Top Layer (02_Top.gbr)

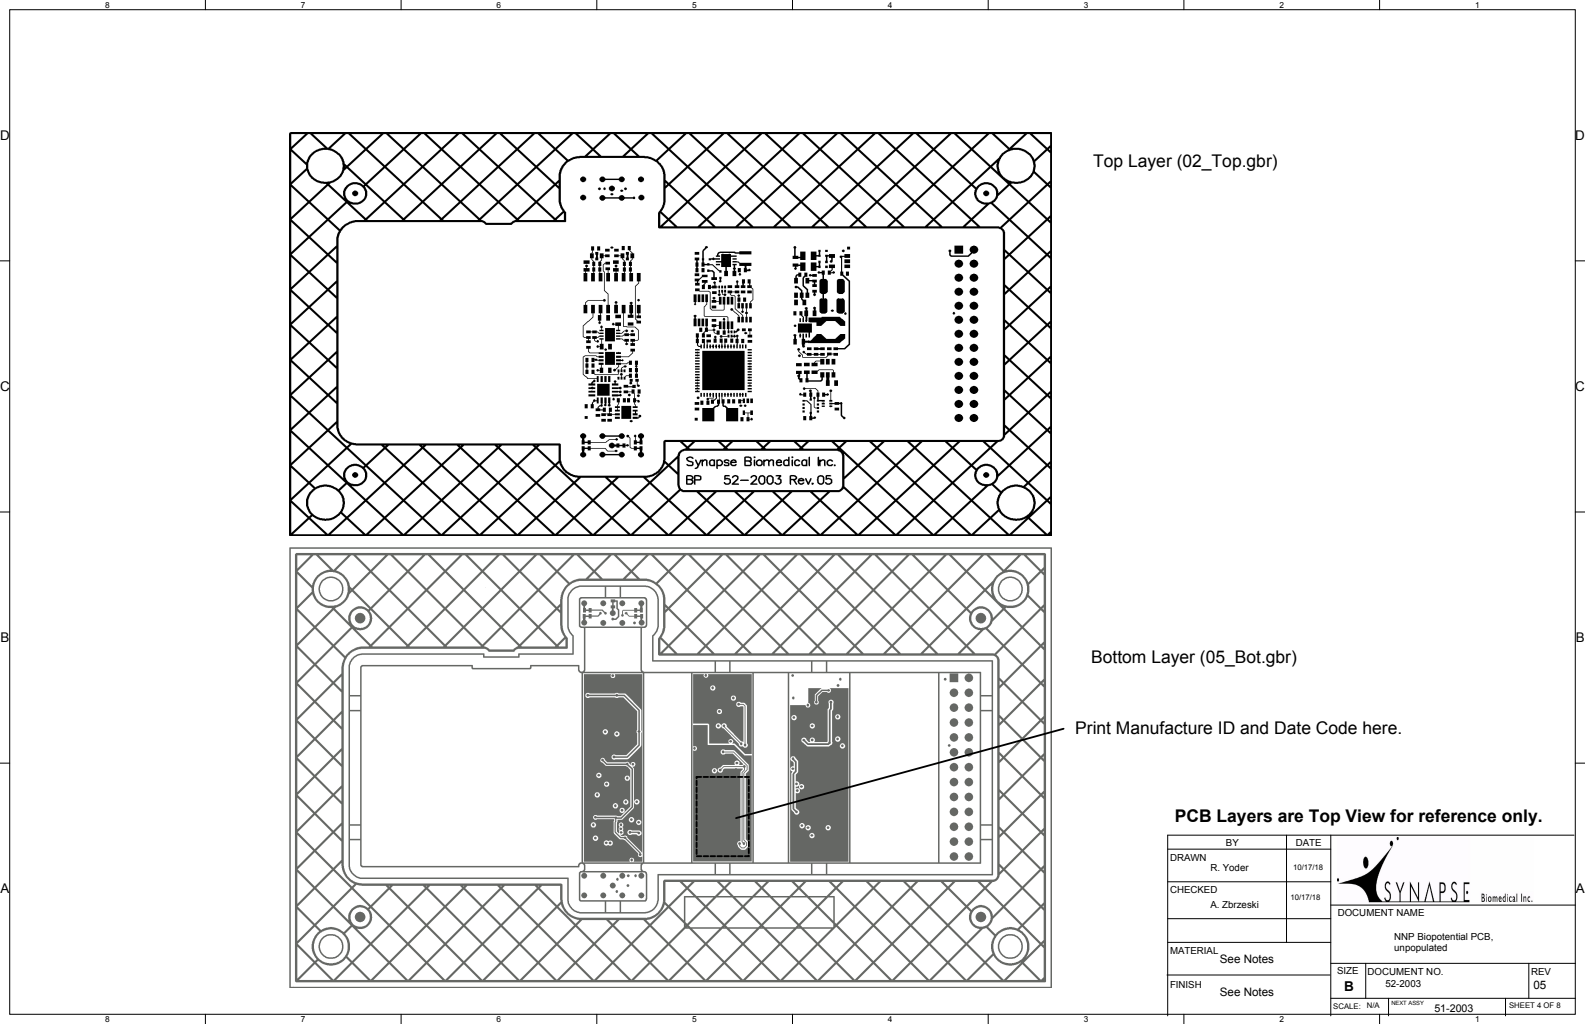
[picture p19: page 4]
DATE; DOCUMENT NAME

Bottom Layer (05_Bot.gbr)

Print Manufacture ID and Date Code here.

PCB Layers are Top View for reference only.

DRAWN R. Yoder | 10/17/18

CHECKED A. Zbrzeski | 10/17/18

NNP Biopotential PCB,

## Layer 2, cu (03_LY2(P).gbr)

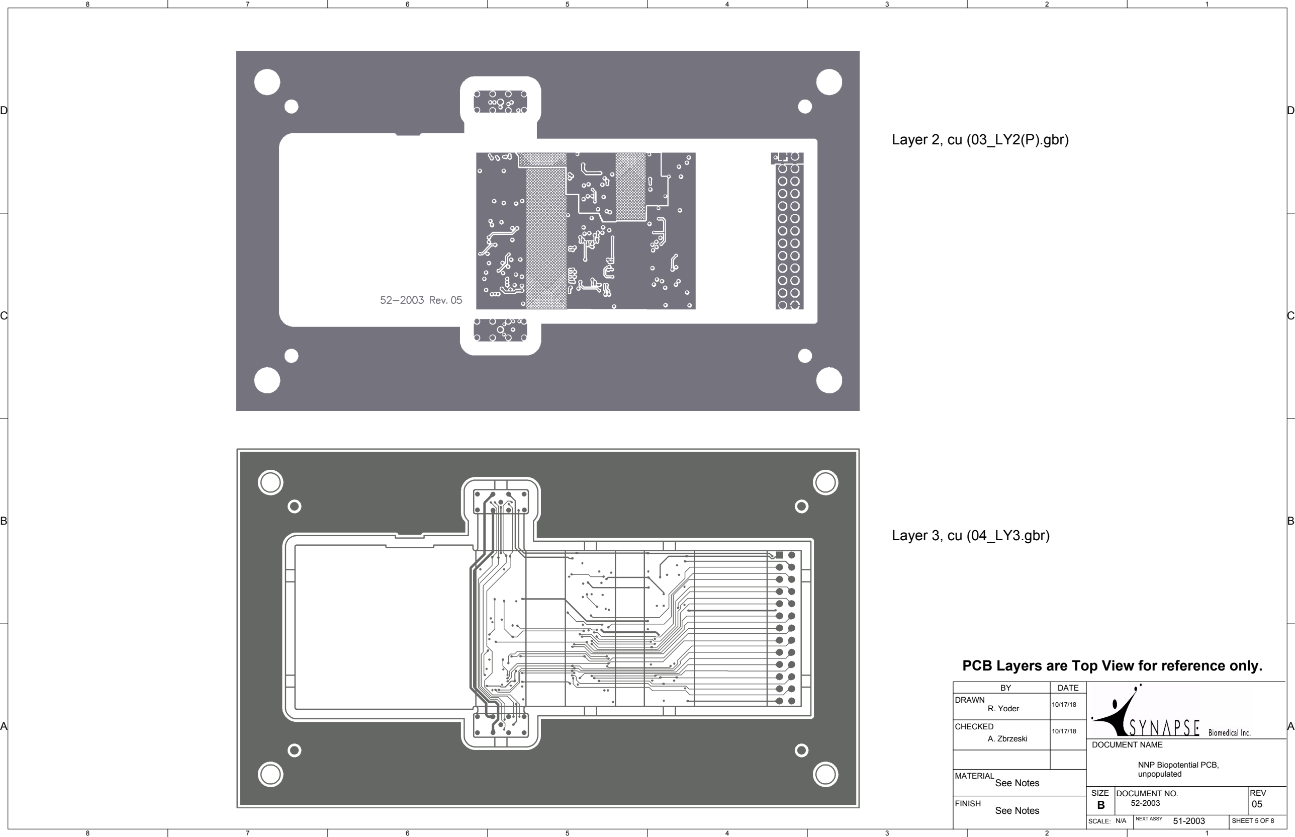
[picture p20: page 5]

D | D
C | C
B | B
A | A
BY | DATE
DRAWN R. Yoder | 10/17/18
CHECKED A. Zbrzeski | 10/17/18

DOCUMENT NAME

NNP Biopotential PCB,

## Layer 3, cu (04_LY3.gbr)

PCB Layers are Top View for reference only.

## Mask Top, (01_MaskTop.gbr)

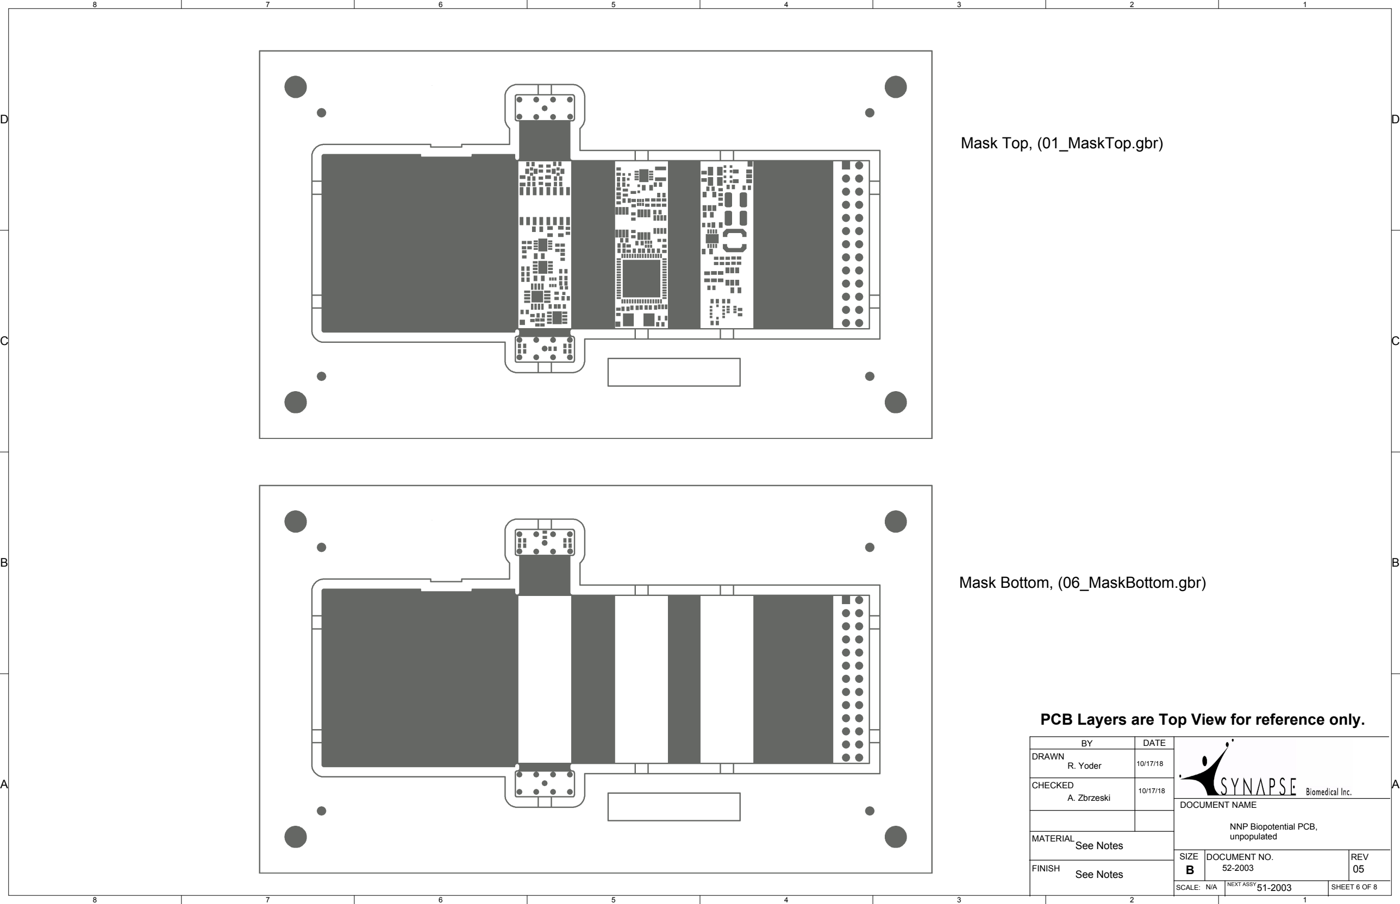
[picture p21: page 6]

D | D
C | C
B | B
A | A
BY | DATE
DRAWN R. Yoder | 10/17/18
CHECKED A. Zbrzeski | 10/17/18

DOCUMENT NAME

NNP Biopotential PCB,

## Mask Bottom, (06_MaskBottom.gbr)

PCB Layers are Top View for reference only.

## Paste Top, (07_PstTop.gbr)

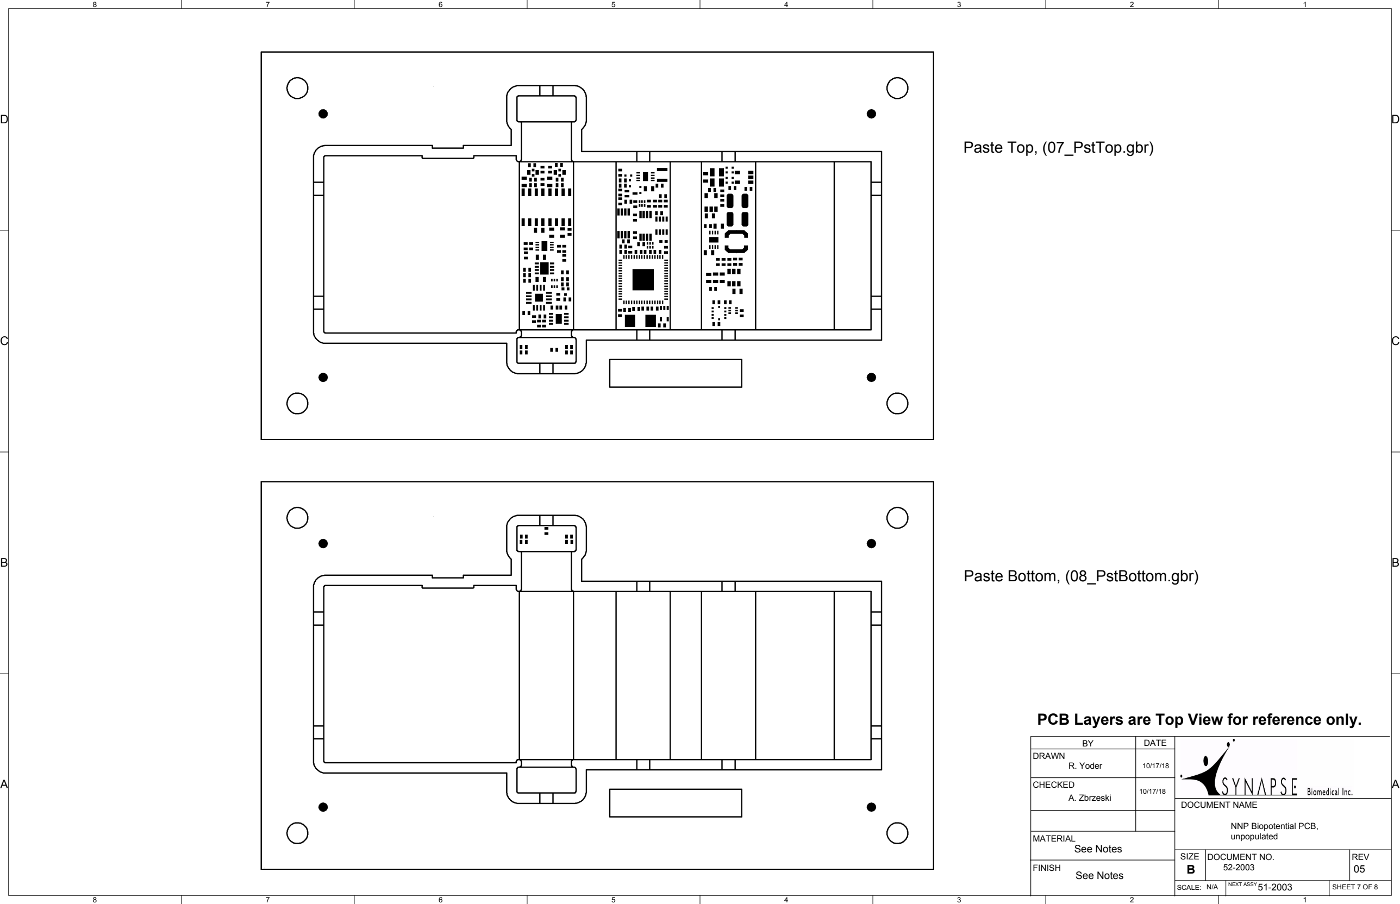
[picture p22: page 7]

D | D
C | C
B | B
A | A
DRAWN R. Yoder | 10/17/18
CHECKED A. Zbrzeski | 10/17/18

NNP Biopotential PCB,

DOCUMENT NAME

BY | DATE
N/A | 51-2003 | SHEET 7 OF 8

## Paste Bottom, (08_PstBottom.gbr)

PCB Layers are Top View for reference only.

D | D
C | C
B | B
A | A
Rigid Area | Flex Area
Solder Mask, 0.5mil
Layer 1, 0.7mil Cu base (0.5 oz), Copper
Dielectric, 2.0mil, VT-47 FR4 .002 H/0
Dielectric, 1.9mil, Prepreg 106 FR406 N.F. | Flex Coverlay Top, LF-7001
Layer 2, 0.7mil (0.5 oz), Copper | Layer 2, 0.7mil (0.5 oz), Copper
Dielectric (Core), 1.0mil, Polyimide AP-8515R | Dielectric (Core), 1.0mil, Polyimide AP-8515R
Layer 3, 0.7mil (0.5 oz), Copper | Layer 3, 0.7mil (0.5 oz), Copper
Dielectric, 1.9mil, Prepreg 106 FR406 N.F. | Flex Coverlay Bottom, LF-7001
Dielectric, 2.0mil, VT-47 FR4 .002 H/0
Layer 4, 0.7mil Cu base (0.5 oz), Copper
Solder Mask, 0.5mil
N/A | 51-2003 | SHEET 8 OF 8
BY | DATE
DRAWN R. Yoder | 10/17/18
CHECKED A. Zbrzeski | 10/17/18

DOCUMENT NAME

NNP Biopotential PCB,

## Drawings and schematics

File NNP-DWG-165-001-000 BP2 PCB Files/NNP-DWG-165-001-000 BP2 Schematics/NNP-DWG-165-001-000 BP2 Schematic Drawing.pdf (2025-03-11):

F | F
E | E
D | D
C | C
B | B
A | A
REVISION | DESCRIPTION | DCN/ECN | DATE THIS DOCUMENT AND THE DATA DISCLOSED HEREIN OR
HEREWITH IS THE PROPERTY OF ALTIUM LIMITED AND MAY BE FREELY DISTRIBUTED IN WHOLE. NO RIGHTS ARE RESERVED OR EXPRESS OR IMPLIED WARANTEE GIVEN.

# Biopotential (BP2) Module Schematic

B | 51-2003-01

TITLE

SIZE | DWG NO.
FILE NAME | SHEET | OF

REV

SCALE:*

*

CAGE CODE

APPROVALS | DATE | PROJECT *
ENG: T. Crish | 10-25-2022
DSN: | K. Kowalski | 10-25-2022
CHK: | | 10-25-2022

REFERENCE DOCUMENTS
BOM:

ASSY DWG:

FAB DWG:

PCB DWG: | *
T. Crish | * PROJECT REVISION: | DOCUMENT REVISION: | DESIGN ITEM:
* | *

xxxx

1 | Initial Release equivalent to CWRU BP2B | -
| See Note 1, DCN 101
| | 3 | See Note 2, DCN 101
| | 4 | See Note 3, DCN 107
| | 5 | See Note 4, DCN 101 | 101
| | 6 | See Note 5, DCN 107 | 107
| | 7 | See Note 6, DCN 121 | 121
| | 8 | See Note 7, DCN 151 | 151

# Biopotential Module ~ 2-channel (BP2)

## Note 1, Rev. 2

2. Moved rail holdup capacitor (C3 and C5) to the front end of the current sense resistor.
3. Added a bypass capacitor (C17) to the network sense negative rail of the LDO (U9).
4. Replaced positive network rail LDO (U3) with a stepdown DC/DC converter.

## 5. Added high side rail switch (Q2) to control the AVDD and n3V3 power supplies for the

Biopotential Amplifier circuit.

6. Added control signal (AVDD_ctrl) from Microcontroller (U11) for high side rail switch.
7. Removed some zero ohm resistors: R12; R13; R19; R30; R37.
8. Changed n3V3 control from switched AVDD to Microcontroller (U11) pin 38, I/O Port C3.
9. Removed zero ohm resistors from shut down input of U12, pin 5.
10. Changed C33 package size from 0603 to 0402..
11. Changed part numbers of several resistors and capacitors for for manufacture and supplier conformity.
12. Changed Resistors R1 - R10 from 0.0ohm to Do Not Populate (DNP).

## Note 2 Rev. 3

## Note 3 Rev. 4

13. Changed C26 from 2.2uF to 1.0uF to prevent transients on the positive analog rail when the AVDD power supply is turned on.
14. Changed C28, C30 and C31 from 10uF to 1.0uF to prevent transients on the negative analog rail when the n3V3 power supply is turned on.
15. Added SBI part numbers to all components.

## Note 4, Rev. 5

16. Changed Manufacturer and Supplier part numbers for C1 and C6 from GRM2165C2A101JA1D to GRM155R71C104KA88D and 490-1599-6-ND to 490-3261-6-ND.
17. Remove Power-up reset circuit C18, R26, and U10. Request from CWRU, report “BP2B Skywire

## Tissue Power Control - Engineering Report 160520 Rev B.docx”

18. Change value of C3 and C5 from 47uF to 22uF.

## Note 0, Rev. 1 1. Initial Release

## Note 5, Rev 06

19. Changed Manufacturer and Supplier part numbers for C2, C14, C15, C28, C30 and C31 from Murata

## Electronics Corp GRM188R71E105KA12D (Digi-Key 490-5307) to TDK Corp CGA3E1X7R1C105K080AC

(Digi-Key 445-12539).

20. Changed Manufacturer and Supplier part numbers for C37, C43, C45, C46, C47, C48 and C54 from

## Murata Electronics Corp GRM155R71C154KA12D (Digi-Key 490-5307) to Samsung Corp CL05B154KO5NNNC (Digi-Key 490-5955)

## Note 6, Rev 07

21. Changed Manufacturer and Supplier part numbers for C40 and C51 from Johanson Dielectric Inc. 500X14W103MV4T to Johanson Dielectric Inc. 500X14W221MV4T (Digi-Key 500X14W221MV4T-ND).

BIOPOTENTIAL MODULE

ENCLOSURE = AMPLIFIER
REFERENCE

-21
NETWORK
POWER

-11
NETWORK
DATA

### POWER CONDITIONING SYSTEMS

-22 3V3
POWER

-23 n3V3
POWER

-24 1V65
REFERENCE

-41
UCONTROLLER

-42 DIGITAL
PERIPHERALS

-43 ANALOG
PERIPHERALS

-61
BIOPOTENTIAL
AMPLIFIER

-1/-2
HEADERS

### PROCESSING

### NON-TISSUE INTERFACES

### TISSUE

INTERFACE | TISSUE

ENCLOSURE = AMPLIFIER
REFERENCE

### fixed polarity variable amplitude analog signal

## ANALOG SIGNALS

### bidirectional unidirectional

## ANALOG CURRENT FLOW or

## DIGITAL SIGNALS

### high level true

### unidirectional

### fixed polarity constant amplitude analog signal

### FESCAN bus power and data signal

## MIXED SIGNALS

### low level true pulse width modulated

### reversing polarity variable amplitude analog signal

## DIGITAL SIGNAL DIRECTION

### biopotential signal

22. Added R57 1M ohm resistor and R58 1M ohm resistor. R57 (Page 5) is hand-soldered across pins 4 and 5 of U12. R58 (Page 3) is hand-soldered across the gate and source of Q2.

## Note 7, Rev 08
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

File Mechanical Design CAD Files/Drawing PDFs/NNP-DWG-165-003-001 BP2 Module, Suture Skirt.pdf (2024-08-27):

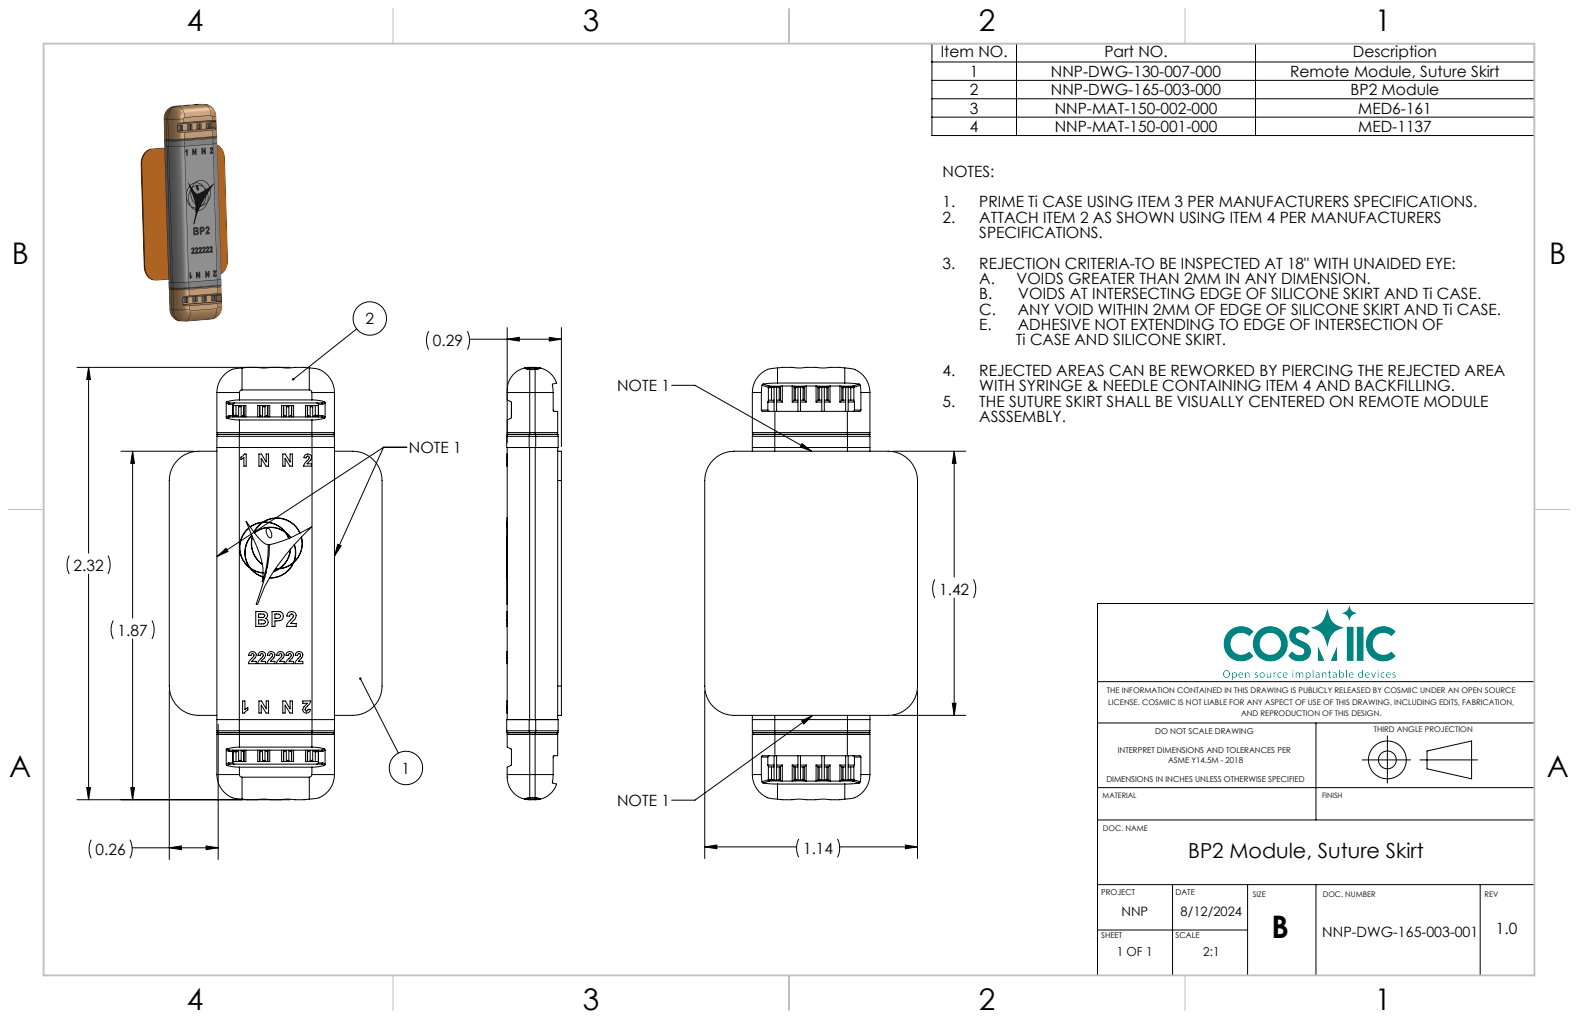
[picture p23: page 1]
NOTE 1; DOC. NUMBER; REV; DOC. NAME; ASME Y14.5M - 2018; NNP-DWG-165-003-001 1.0; BP2 Module, Suture Skirt

Item NO. | Part NO. | Description
1 | NNP-DWG-130-007-000 | Remote Module, Suture Skirt
2 | NNP-DWG-165-003-000 | BP2 Module
3 | NNP-MAT-150-002-000 | MED6-161
4 | NNP-MAT-150-001-000 | MED-1137

NOTES:
1. PRIME Ti CASE USING ITEM 3 PER MANUFACTURERS SPECIFICATIONS.
2. ATTACH ITEM 2 AS SHOWN USING ITEM 4 PER MANUFACTURERS
SPECIFICATIONS.
3. REJECTION CRITERIA-TO BE INSPECTED AT 18" WITH UNAIDED EYE:
A. VOIDS GREATER THAN 2MM IN ANY DIMENSION.
B. VOIDS AT INTERSECTING EDGE OF SILICONE SKIRT AND Ti CASE.
C. ANY VOID WITHIN 2MM OF EDGE OF SILICONE SKIRT AND Ti CASE.
E. ADHESIVE NOT EXTENDING TO EDGE OF INTERSECTION OF
Ti CASE AND SILICONE SKIRT.

4. REJECTED AREAS CAN BE REWORKED BY PIERCING THE REJECTED AREA
WITH SYRINGE & NEEDLE CONTAINING ITEM 4 AND BACKFILLING.
5. THE SUTURE SKIRT SHALL BE VISUALLY CENTERED ON REMOTE MODULE
ASSSEMBLY.

THE INFORMATION CONTAINED IN THIS DRAWING IS PUBLICLY RELEASED BY COSMIIC UNDER AN OPEN SOURCE
LICENSE. COSMIIC IS NOT LIABLE FOR ANY ASPECT OF USE OF THIS DRAWING, INCLUDING EDITS, FABRICATION,

AND REPRODUCTION OF THIS DESIGN.

DO NOT SCALE DRAWING

THIRD ANGLE PROJECTION

INTERPRET DIMENSIONS AND TOLERANCES PER

DIMENSIONS IN INCHES UNLESS OTHERWISE SPECIFIED

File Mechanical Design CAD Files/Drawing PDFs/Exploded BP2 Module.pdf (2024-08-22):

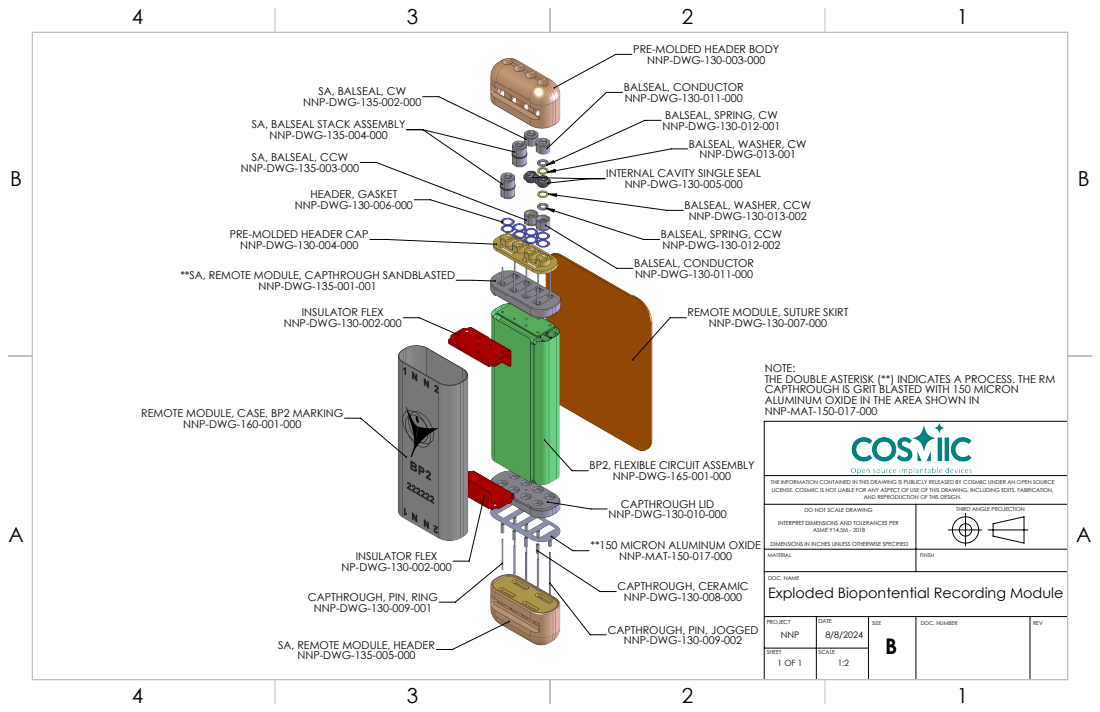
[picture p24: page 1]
HEADER, GASKET; INSULATOR FLEX; CAPTHROUGH, CERAMIC; DOC. NUMBER; REV; DOC. NAME; ASME Y14.5M - 2018

PRE-MOLDED HEADER BODY
NNP-DWG-130-003-000
BALSEAL, CONDUCTOR
NNP-DWG-130-011-000
BALSEAL, SPRING, CW
NNP-DWG-130-012-001
BALSEAL, WASHER, CW
NNP-DWG-013-001

SA, BALSEAL, CW
NNP-DWG-135-002-000

SA, BALSEAL STACK ASSEMBLY
NNP-DWG-135-004-000
SA, BALSEAL, CCW
NNP-DWG-135-003-000

INTERNAL CAVITY SINGLE SEAL
NNP-DWG-130-005-000

BALSEAL, WASHER, CCW
NNP-DWG-130-013-002
BALSEAL, SPRING, CCW
NNP-DWG-130-012-002

PRE-MOLDED HEADER CAP
NNP-DWG-130-004-000

**SA, REMOTE MODULE, CAPTHROUGH SANDBLASTED

REMOTE MODULE, SUTURE SKIRT
NNP-DWG-130-007-000

NOTE:
THE DOUBLE ASTERISK (**) INDICATES A PROCESS. THE RM
CAPTHROUGH IS GRIT BLASTED WITH 150 MICRON
ALUMINUM OXIDE IN THE AREA SHOWN IN
NNP-MAT-150-017-000

REMOTE MODULE, CASE, BP2 MARKING
NNP-DWG-160-001-000

BP2, FLEXIBLE CIRCUIT ASSEMBLY
NNP-DWG-165-001-000
CAPTHROUGH LID
NNP-DWG-130-010-000

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

AND REPRODUCTION OF THIS DESIGN.

DO NOT SCALE DRAWING

THIRD ANGLE PROJECTION

INTERPRET DIMENSIONS AND TOLERANCES PER

**150 MICRON ALUMINUM OXIDE

DIMENSIONS IN INCHES UNLESS OTHERWISE SPECIFIED
Exploded Biopontential Recording Module

CAPTHROUGH, PIN, RING
NNP-DWG-130-009-001

CAPTHROUGH, PIN, JOGGED
NNP-DWG-130-009-002

SA, REMOTE MODULE, HEADER
NNP-DWG-135-005-000

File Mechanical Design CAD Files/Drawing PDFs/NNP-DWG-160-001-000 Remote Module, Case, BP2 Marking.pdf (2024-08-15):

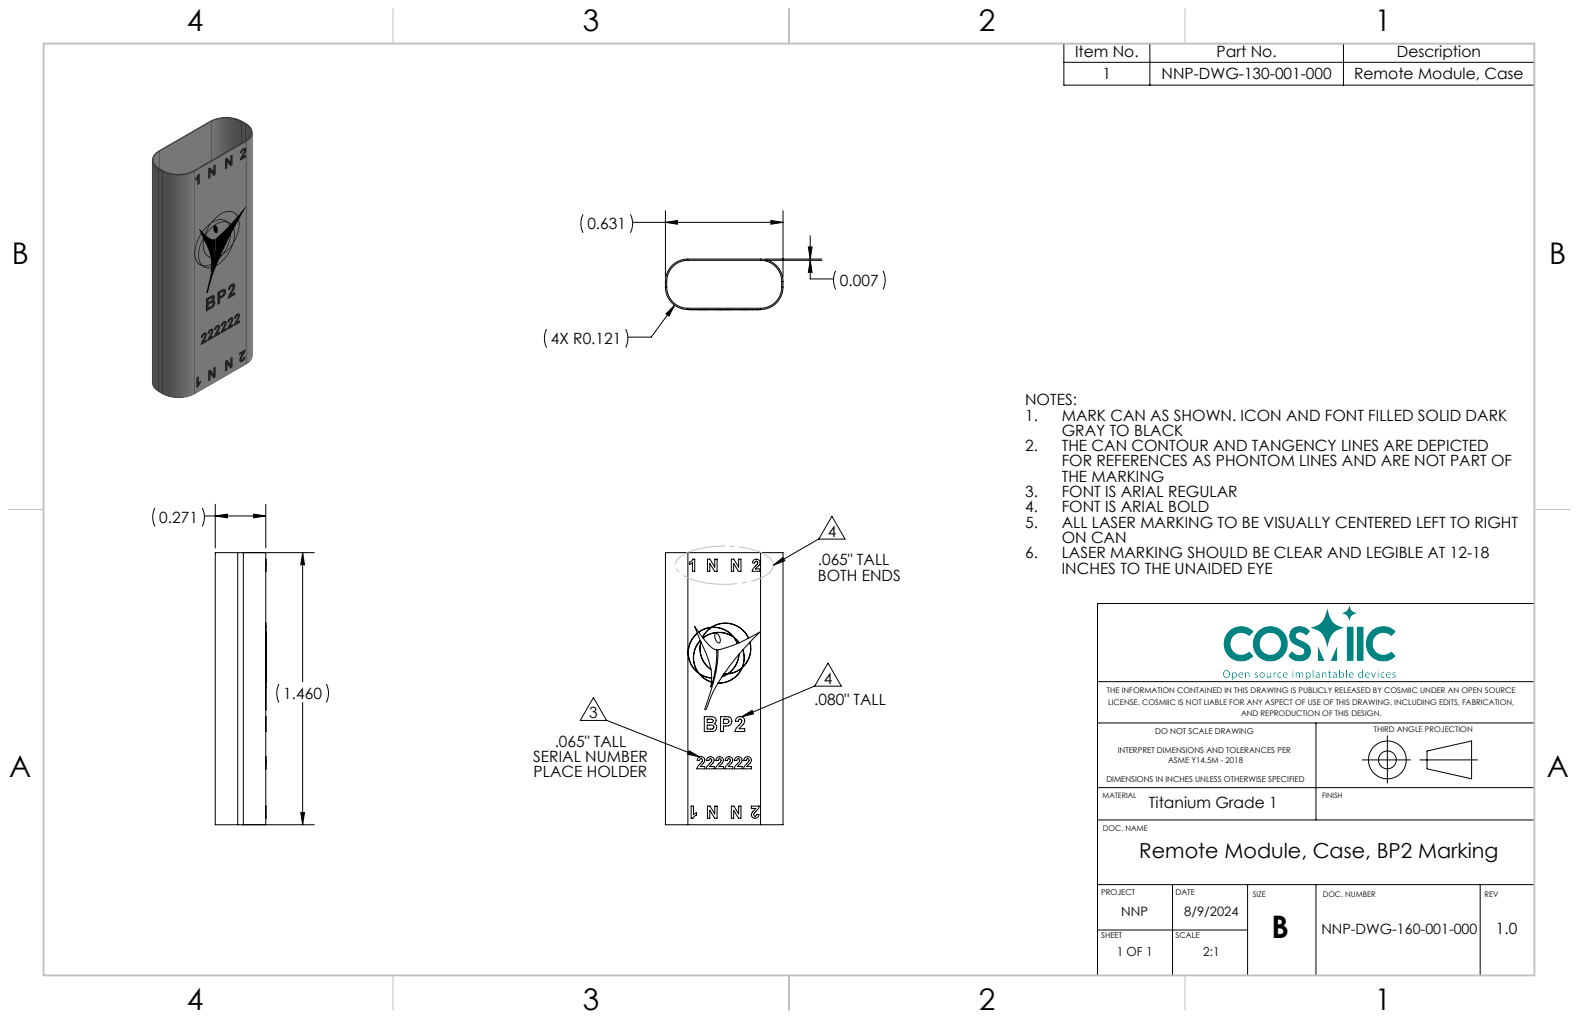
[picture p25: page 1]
.065" TALL BOTH ENDS; .080" TALL; .065" TALL SERIAL NUMBER PLACE HOLDER; DOC. NUMBER; REV; DOC. NAME

Item No. | Part No. | Description
1 | NNP-DWG-130-001-000 | Remote Module, Case

NOTES:
1. MARK CAN AS SHOWN. ICON AND FONT FILLED SOLID DARK
GRAY TO BLACK
2. THE CAN CONTOUR AND TANGENCY LINES ARE DEPICTED
FOR REFERENCES AS PHONTOM LINES AND ARE NOT PART OF
THE MARKING
3. FONT IS ARIAL REGULAR
4. FONT IS ARIAL BOLD
5. ALL LASER MARKING TO BE VISUALLY CENTERED LEFT TO RIGHT
ON CAN
6. LASER MARKING SHOULD BE CLEAR AND LEGIBLE AT 12-18
INCHES TO THE UNAIDED EYE

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

AND REPRODUCTION OF THIS DESIGN.

DO NOT SCALE DRAWING

THIRD ANGLE PROJECTION

INTERPRET DIMENSIONS AND TOLERANCES PER

ASME Y14.5M - 2018
Titanium Grade 1
Remote Module, Case, BP2 Marking
NNP-DWG-160-001-000

DIMENSIONS IN INCHES UNLESS OTHERWISE SPECIFIED

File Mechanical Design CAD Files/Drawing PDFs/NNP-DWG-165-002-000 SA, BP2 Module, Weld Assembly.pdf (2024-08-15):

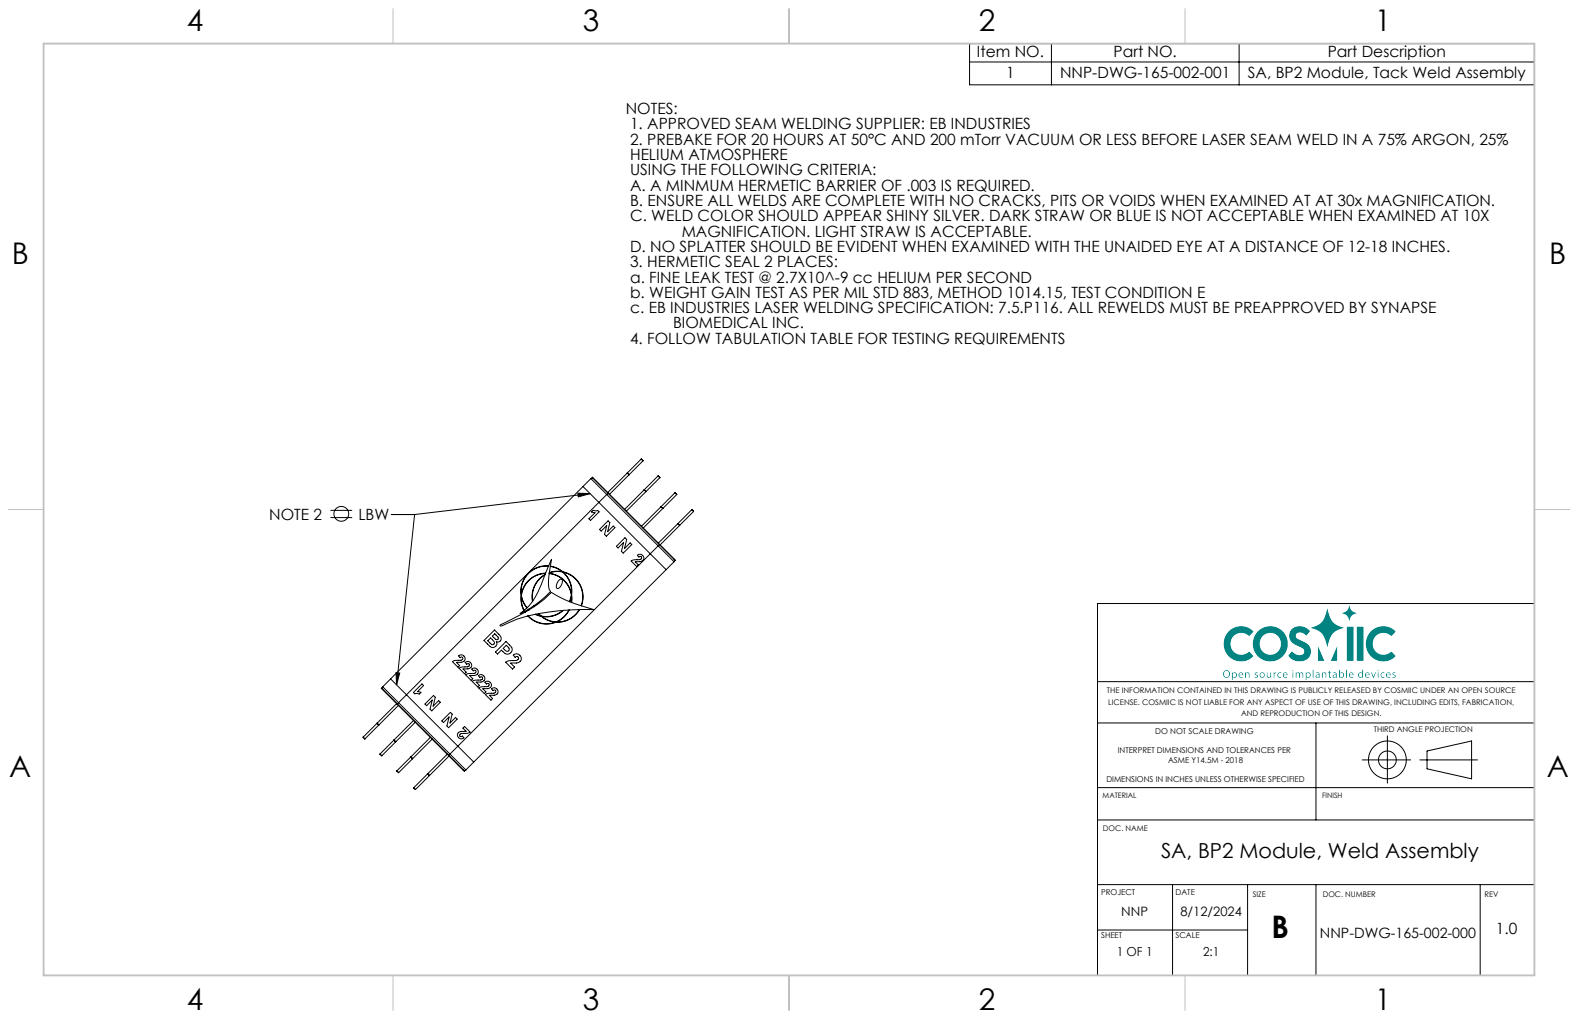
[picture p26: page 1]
NOTE 2; LBW; DOC. NUMBER; REV; DOC. NAME; ASME Y14.5M - 2018

Item NO. | Part NO. | Part Description
1 | NNP-DWG-165-002-001 | SA, BP2 Module, Tack Weld Assembly

NOTES:
1. APPROVED SEAM WELDING SUPPLIER: EB INDUSTRIES
2. PREBAKE FOR 20 HOURS AT 50°C AND 200 mTorr VACUUM OR LESS BEFORE LASER SEAM WELD IN A 75% ARGON, 25%
HELIUM ATMOSPHERE
USING THE FOLLOWING CRITERIA:
A. A MINMUM HERMETIC BARRIER OF .003 IS REQUIRED.
B. ENSURE ALL WELDS ARE COMPLETE WITH NO CRACKS, PITS OR VOIDS WHEN EXAMINED AT AT 30x MAGNIFICATION.
C. WELD COLOR SHOULD APPEAR SHINY SILVER. DARK STRAW OR BLUE IS NOT ACCEPTABLE WHEN EXAMINED AT 10X
MAGNIFICATION. LIGHT STRAW IS ACCEPTABLE.
D. NO SPLATTER SHOULD BE EVIDENT WHEN EXAMINED WITH THE UNAIDED EYE AT A DISTANCE OF 12-18 INCHES.
3. HERMETIC SEAL 2 PLACES:
a. FINE LEAK TEST @ 2.7X10^-9 cc HELIUM PER SECOND
b. WEIGHT GAIN TEST AS PER MIL STD 883, METHOD 1014.15, TEST CONDITION E
c. EB INDUSTRIES LASER WELDING SPECIFICATION: 7.5.P116. ALL REWELDS MUST BE PREAPPROVED BY SYNAPSE
BIOMEDICAL INC.
4. FOLLOW TABULATION TABLE FOR TESTING REQUIREMENTS

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

AND REPRODUCTION OF THIS DESIGN.

DO NOT SCALE DRAWING

THIRD ANGLE PROJECTION

INTERPRET DIMENSIONS AND TOLERANCES PER

DIMENSIONS IN INCHES UNLESS OTHERWISE SPECIFIED
SA, BP2 Module, Weld Assembly
NNP-DWG-165-002-000

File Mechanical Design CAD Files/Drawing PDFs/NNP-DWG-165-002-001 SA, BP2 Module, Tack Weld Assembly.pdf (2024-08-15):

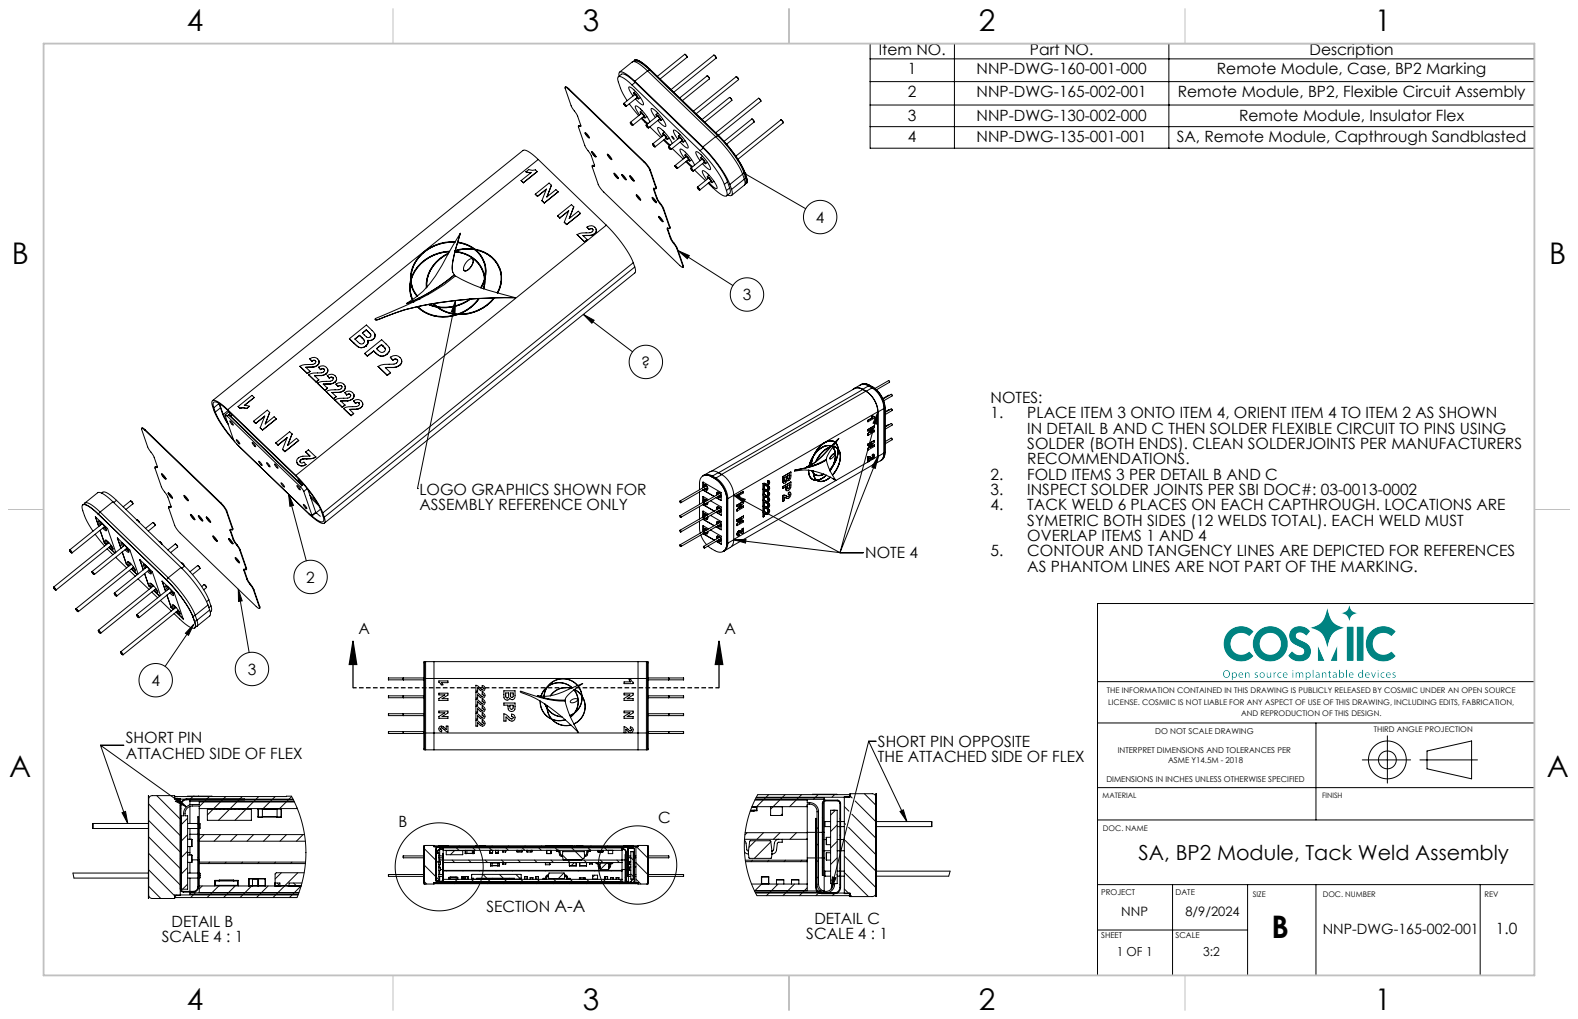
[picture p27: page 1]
NOTE 4; SECTION A-A; DETAIL B SCALE 4 : 1; DETAIL C SCALE 4 : 1; DOC. NUMBER; REV; DOC. NAME; ASME Y14.5M - 2018

Item NO. | Part NO. | Description
1 | NNP-DWG-160-001-000 | Remote Module, Case, BP2 Marking
2 | NNP-DWG-165-002-001 | Remote Module, BP2, Flexible Circuit Assembly
3 | NNP-DWG-130-002-000 | Remote Module, Insulator Flex
4 | NNP-DWG-135-001-001 | SA, Remote Module, Capthrough Sandblasted

NOTES:
1. PLACE ITEM 3 ONTO ITEM 4, ORIENT ITEM 4 TO ITEM 2 AS SHOWN
IN DETAIL B AND C THEN SOLDER FLEXIBLE CIRCUIT TO PINS USING
SOLDER (BOTH ENDS). CLEAN SOLDERJOINTS PER MANUFACTURERS
RECOMMENDATIONS.
2. FOLD ITEMS 3 PER DETAIL B AND C
3. INSPECT SOLDER JOINTS PER SBI DOC#: 03-0013-0002
4. TACK WELD 6 PLACES ON EACH CAPTHROUGH. LOCATIONS ARE
SYMETRIC BOTH SIDES (12 WELDS TOTAL). EACH WELD MUST
OVERLAP ITEMS 1 AND 4
5. CONTOUR AND TANGENCY LINES ARE DEPICTED FOR REFERENCES
AS PHANTOM LINES ARE NOT PART OF THE MARKING.

LOGO GRAPHICS SHOWN FOR
ASSEMBLY REFERENCE ONLY

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

AND REPRODUCTION OF THIS DESIGN.

SHORT PIN
ATTACHED SIDE OF FLEX

DO NOT SCALE DRAWING

THIRD ANGLE PROJECTION

SHORT PIN OPPOSITE
THE ATTACHED SIDE OF FLEX

INTERPRET DIMENSIONS AND TOLERANCES PER

DIMENSIONS IN INCHES UNLESS OTHERWISE SPECIFIED
SA, BP2 Module, Tack Weld Assembly
NNP-DWG-165-002-001

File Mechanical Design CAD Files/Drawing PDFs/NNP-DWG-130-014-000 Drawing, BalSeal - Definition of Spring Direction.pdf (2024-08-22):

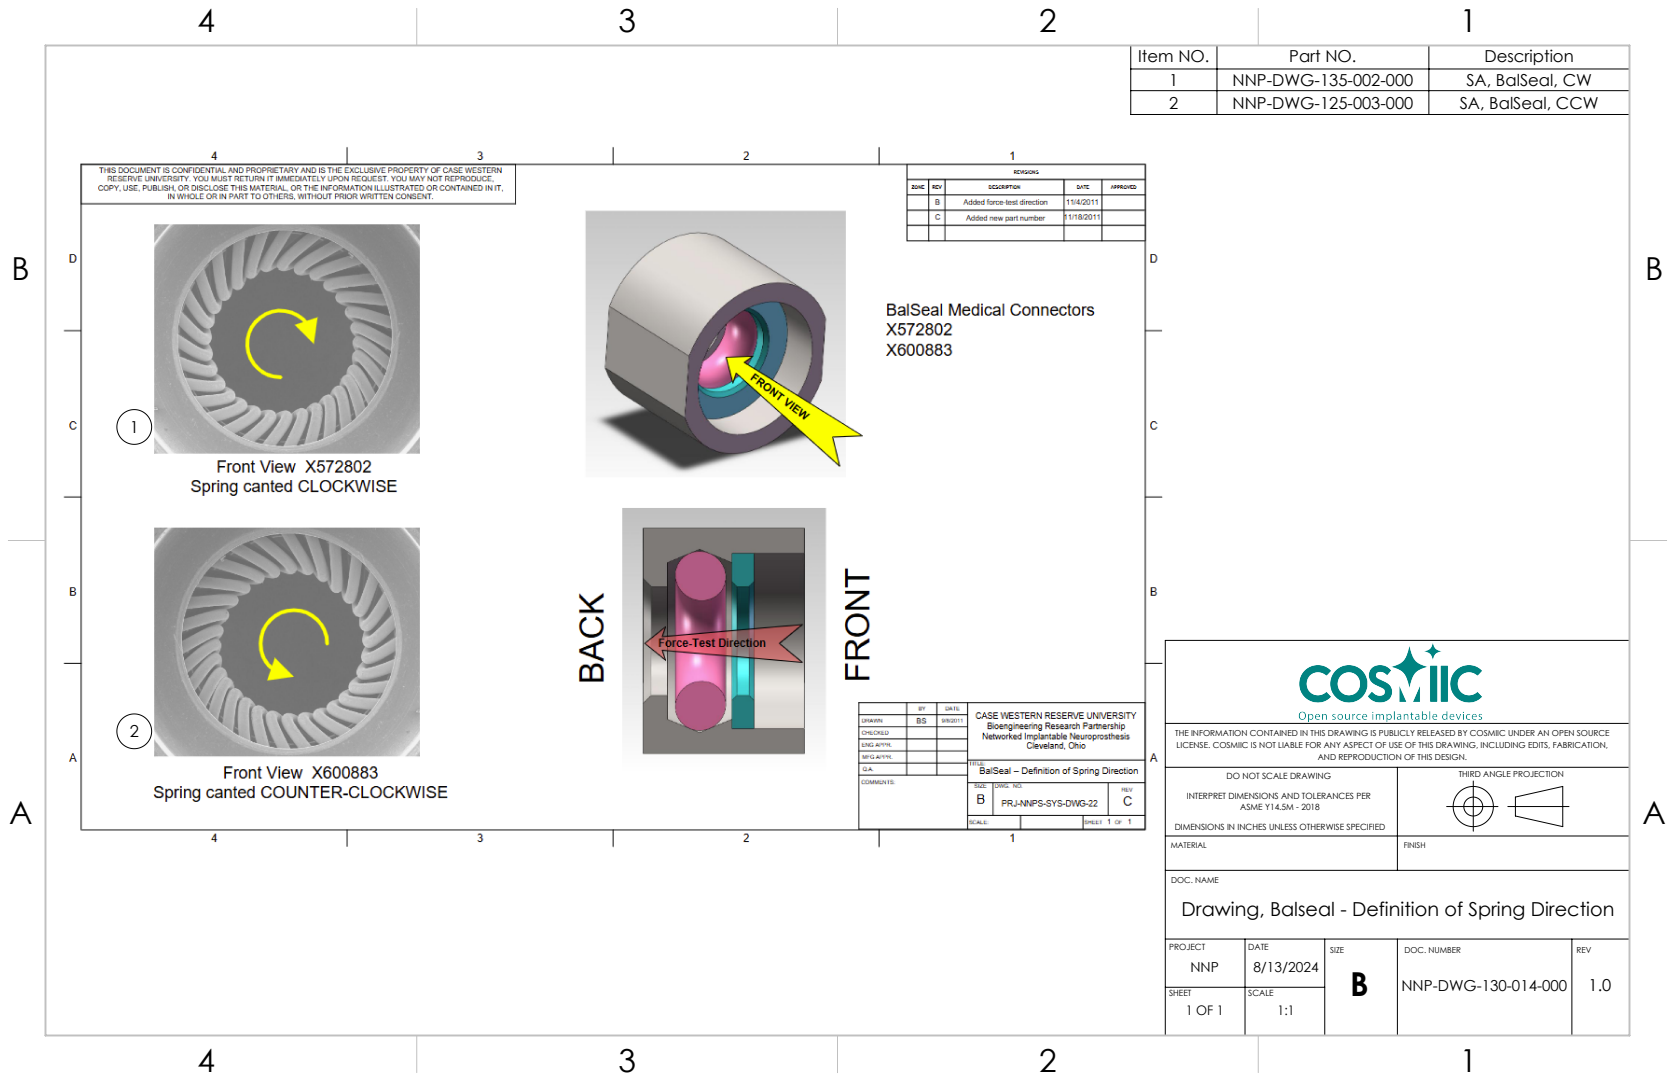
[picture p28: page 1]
DOC. NUMBER; REV; ASME Y14.5M - 2018

Item NO. | Part NO. | Description
1 | NNP-DWG-135-002-000 | SA, BalSeal, CW
2 | NNP-DWG-125-003-000 | SA, BalSeal, CCW

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

AND REPRODUCTION OF THIS DESIGN.

DO NOT SCALE DRAWING

THIRD ANGLE PROJECTION

INTERPRET DIMENSIONS AND TOLERANCES PER

DIMENSIONS IN INCHES UNLESS OTHERWISE SPECIFIED

DOC. NAME
Drawing, Balseal - Definition of Spring Direction

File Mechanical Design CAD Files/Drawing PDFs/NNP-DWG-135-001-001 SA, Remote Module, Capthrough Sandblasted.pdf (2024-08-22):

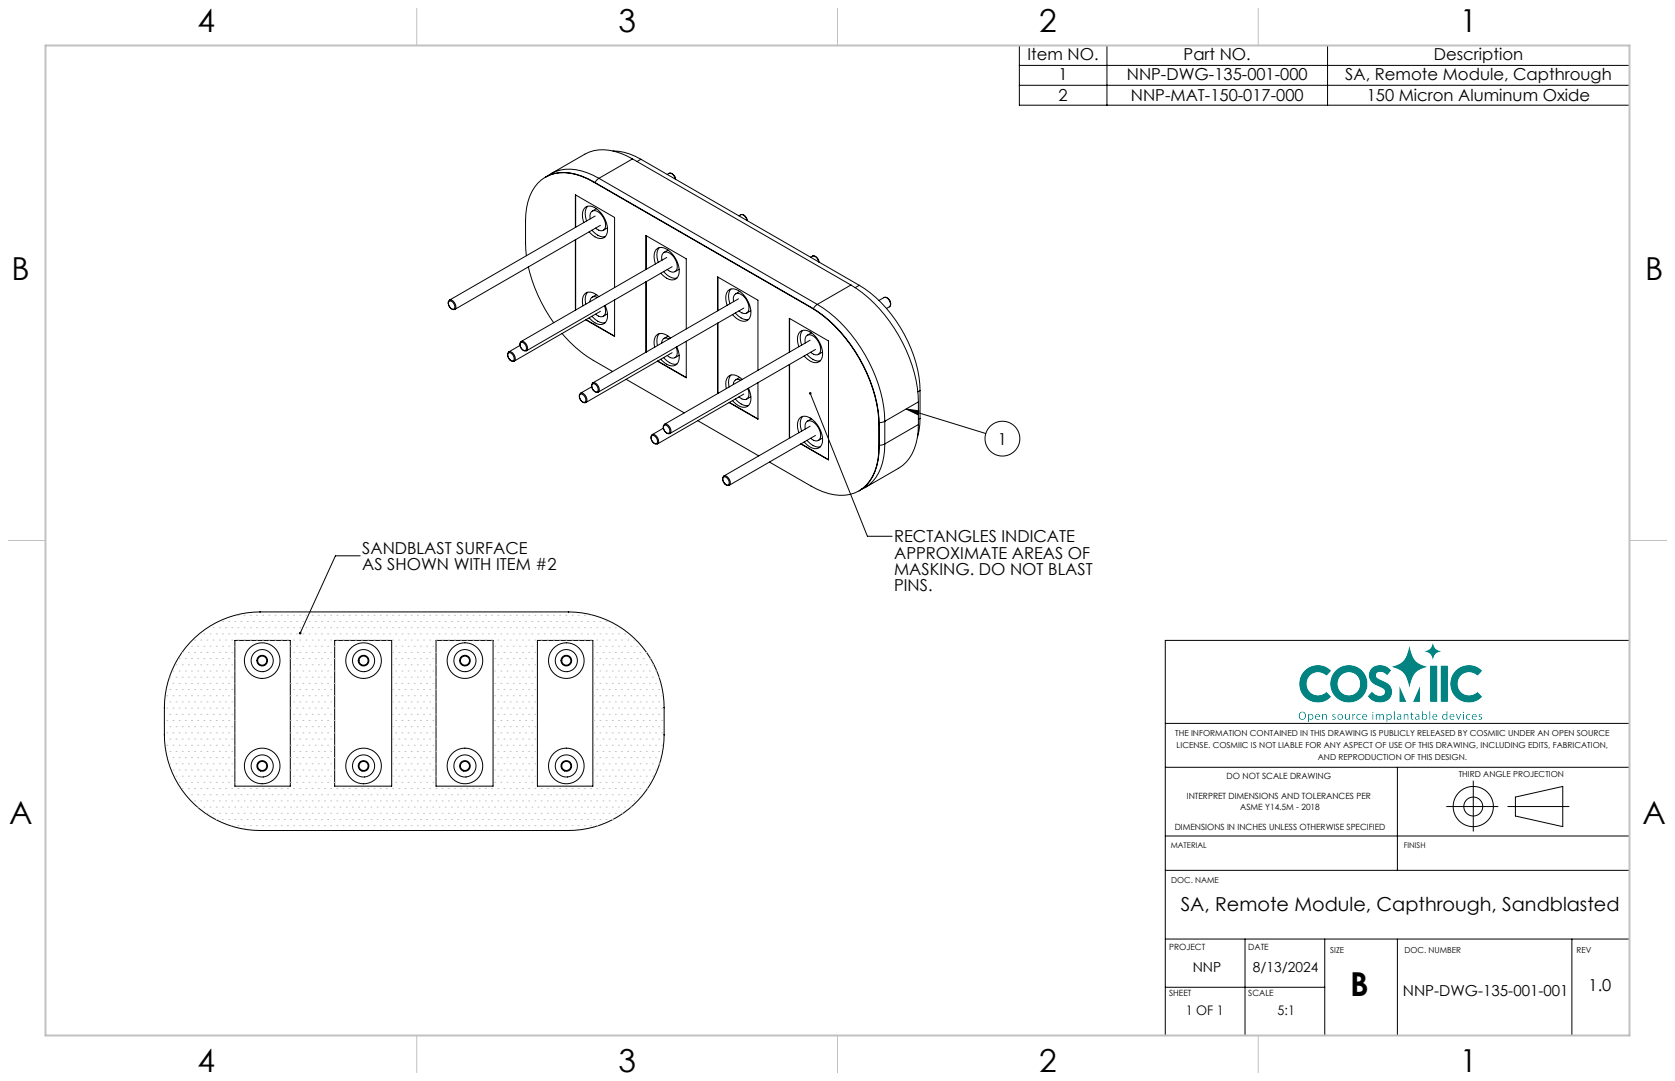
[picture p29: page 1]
DOC. NUMBER; REV; ASME Y14.5M - 2018

Item NO. | Part NO. | Description
1 | NNP-DWG-135-001-000 | SA, Remote Module, Capthrough
2 | NNP-MAT-150-017-000 | 150 Micron Aluminum Oxide

RECTANGLES INDICATE
APPROXIMATE AREAS OF
MASKING. DO NOT BLAST
PINS.

SANDBLAST SURFACE
AS SHOWN WITH ITEM #2

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

AND REPRODUCTION OF THIS DESIGN.

DO NOT SCALE DRAWING

THIRD ANGLE PROJECTION

INTERPRET DIMENSIONS AND TOLERANCES PER

DIMENSIONS IN INCHES UNLESS OTHERWISE SPECIFIED

DOC. NAME
SA, Remote Module, Capthrough, Sandblasted

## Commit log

2024-08-12 Uploading BP2 CAD
    [NNP-DWG-130-001-000 Remote Module, Case, No Marking.SLDPRT, NNP-DWG-130-001-000 Remote Module, Case, No Marking.STEP, NNP-DWG-130-001-000 Remote Module, Case.S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]
2024-08-13 Uploading RM drawings
    [NNP-DWG-130-015-000 Drawing, BalSeal - Definition of Spring Dircetion.SLDDRW, NNP-DWG-135-001-001 SA, Remote Module, Capthrough Sandblasted.SLDDRW, NNP-DWG-135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]
2024-08-14 updating balseal drawings with latest revision
    [NNP-DWG-130-015-000 Drawing, BalSeal - Definition of Spring Dircetion.SLDDRW, NNP-DWG-130-015-000 Drawing, BalSeal - Definition of Spring Direction.SLDDRW, NNP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]
2024-08-15 Updating BP2 fila part numbers to be unique to BP2
    [NNP-DWG-130-001-002 Remote Module, Case, BP2 Marking.SLDASM, NNP-DWG-130-001-002 Remote Module, Case, BP2 Marking.STEP, NNP-DWG-135-009-000 SA, BP2 Module, Wel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]
2024-08-22 Updating part numbers based on changing 150 micron to a MAT instead of DWG
    [NNP-DWG-130-014-000 Capthrough, 150 Micron Aluminum Oxide.SLDPRT, NNP-DWG-130-014-000 Capthrough, 150 Micron Aluminum Oxide.STEP, NNP-DWG-130-014-000 Drawing, 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]
2025-03-11 Posting existing BP2 PCB design files
    [01_MaskTop_DI.gbr, 02_R_Top.gbr, 03_R_Ly2.gbr, 04_R_Ly3.gbr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]
